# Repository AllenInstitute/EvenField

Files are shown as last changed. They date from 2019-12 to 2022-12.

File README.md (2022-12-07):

# EvenField - An easy, cost effective alternative to commercial based illumination systems for fluorescence microscopy

Coherent laser sources with Gaussian output profiles have been a preferred choice in many optical microscopy systems due to their high spatial intensity and monochromaticity. While these traits can beneficial in many applications, the high spatial coherence of these lasers results in interference effects as the light propagates through various optics toward the sample plane. These inference patterns superimposed onto the Gaussian laser profile result in an uneven illumination of the sample that get transferred into resulting images. For applications such as single molecule fluorescence imaging, the resulting field inhomogeneity  often clouds the signal that is to be detected. In addition, when these sources are used for imaging large areas that require tiling of multiple fields of view, the circular 2D illumination profile excites a larger field of view than is captured by the camera resulting in additional, unneeded photobleaching of these areas.

A simple deployment of a square multimode fiber between the illumination source and destination corrects this issue; however, the propogation of multiple laser modes through the fiber increases the potential for interference and results in additional laser speckle noise in the output beam. Researchers have developed several solutions to circumvent the laser speckle problem including, fiber vibration, tunable oscillating lenses, and spinning diffusers. 

We test some of these solutions and compare them to a commercial product, the Borealis system by Andor. 

----

Our full evaluation of this system can be found in our preprint : 
https://www.biorxiv.org/content/10.1101/2021.04.20.440683v1
  
---
  
We converged on a simple, cost-effective solution which we call the EvenField Illumination system. 

## So you're interested in building the EvenField system? ...We've got you covered.

This repository contains all of the information you will need to get started on building and employing the Evenfield system in your lab. This system can be used on a traditional, commercial laser launch or can be combined with the open source [Nicolase 3500] diode combiner and fiber launch for a cost effective, total solution for your illumination needs.

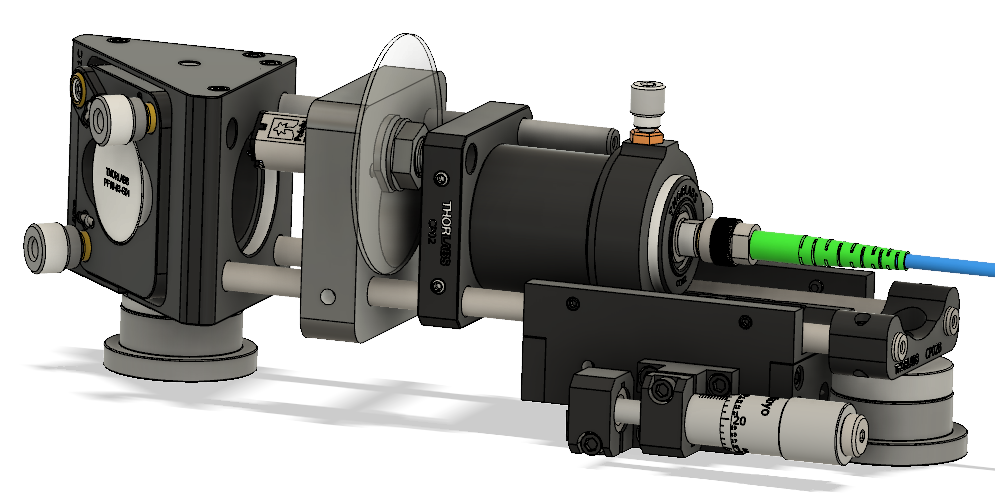
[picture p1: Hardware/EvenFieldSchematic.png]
EvenField System


#### Hardware:
A complete list of associated hardware can be found [here](/Hardware).

This folder contains everything needed to build the EvenField system, including: 

* A complete [bill of materials] (optics and mounts)
* CAD renderings and .STEP files for the spinning diffuser component
* Details on custom optical fiber from Mitsubishi Cable Industries (MCI).
* Illuminator module for easy sensor size matching
* *Coming Soon:* Optical alignment guide 

#### Analysis:
The analysis code used for the EvenField publication has also been provided within this repo and may prove useful for evaluating the field flatness of your system. Code was written in Python and can be found [here].

[Nicolase 3500]: https://github.com/PRNicovich/NicoLase 
[bill of materials]: https://github.com/AllenInstitute/EvenField/blob/master/Hardware/EvenField%20Parts%20List.md
[here]: https://github.com/AllenInstitute/EvenField/tree/master/Analysis

#### Zoom illuminator update
Building on the published EvenField coupler and illuminator design, we implemented a microscope illuminator that features straightforward alignment and sensor-shape matching.  Illumination energy is delivered through an optical fiber - the details of which are not critical for use - and into a homogenizing prism.  The square exit face of this prism is imaged by a commercially-available zoom camera lens and a tube + objective lens pair to the sample plane.  Adjustments to the size and focus of the illumination field are straightfoward using the zoom and focus rings on the camera lens. On its own this assembly provides a simple and cheap square-field illumninator that will work with a wide range of detection camera formats.  Together with the EvenField homogenizer and NicoLase laser launch you can build your own microscopy illumination platform with custom laser power, color, and timing, evenly distributed over a field matching the detection camera FOV.  Add a chassis, cube, objective, and camera, and you've got a fluorescence microscope.

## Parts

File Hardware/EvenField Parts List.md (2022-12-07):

# EvenField V1 Parts List
------------------
### EvenField Speckle Reduction Scheme:
    1 x Edmund Optics #47-989, 0.5° Diffusing Angle 50 mm Dia Mounted (Holographic Diffuser)
    1 x Pololu 3036, 5:1 Micro Metal Gearmotor HPCB 12V (EvenField Version 1 motor, used in manuscript)
    1 x Custom Milled Assembly (see associated CAD)
    
### Optics: 
    1 x Thorlabs PF10-03-G01, Ø1” Protected Aluminum Mirror
    1 x Thorlabs C220TMD-A, f = 11.00 mm, NA = 0.25, Mounted Geltech Aspheric Lens

### Mounting:
    1 x Thorlabs KCB1C, Right-Angle Kinematic Mirror Mount with Smooth Cage Rod Bores
    1 x Thorlabs SM1L10, SM1 Lens Tune 1.00” Thread Depth
    1 x Thorlabs S1TM09, Mounted Aspheric Lens Adapter
    1 x Thorlabs CP02, SM1-Threaded 30 mm Cage Plate
    1 x Thorlabs CT102, XY Translation Mount
    1 x Thorlabs CT1, Cage Translation Stage
    1 x Thorlabs SM05FC, FC/PC Fiber Adapter Plate with External SM05
    1 x Thorlabs CP02B, Snap-On 30 mm Cage Mounting Bracket, 8-32 Tap
    2 x Thorlabs RS05P, Ø1" Pedestal Pillar Post, 1/4"-20 Taps, L = 0.5"
    1 x Thorlabs RS3M, Ø25 mm Post Spacer, Thickness = 3 mm
    1 x Thorlabs RS6M, Ø25 mm Post Spacer, Thickness = 6 mm
    1 x Thorlabs ER3, Cage Assembly Rod, 3” Long
    2 x Thorlabs ER6, Cage Assembly Rod, 6” Long

### Fiber:
    1 x Custom Multimode Square Core Fiber from Mitsubishi Cable Industries, LTD., 600 µm x 600 µm core, 0.15 NA P/N: KV95P2 ST600SQH 
     OR
    1 x Thorlabs M43L05, Ø105 µm, 0.22 NA, Low OH, FC/PC-FC/PC Fiber Patch Cable, 5 m

### Output Collimator:
	  1 x Edmund Optics 88-379, 10X Objective, Nikon CFI Plan Fluor
	   OR
	  1 x Thorlabs PAF2P-18A, FiberPort, FC/PC, f=18.4 mm, 350 - 700 nm, Ø3.01 mm Waist
		       Note: Mitsubishi MM fiber has a very large fiber core (600 µm x 600 µm). Due to its size, using the 10X Objective          
                       is the preferred collimation option to avoid vignetting; however, this option introduces additional optical 
                       alignment complexities. 

### Zoom illuminator:

The following parts form a critical illumiator to couple an output fiber into a square prism, then project the prism exit face to the sample plane.  The following components were used in combination with a Nikon Ti2 and Iris15 camera.  The zoom lens adjustments allow for straightforward matching of the illumination and collection areas with minimal light outside of this region.  Using the square prism avoids the need for a square-core fiber and additional magnification in this application.  

	1 x Thorlabs SM2A54 
	2 x Thorlabs LCP01T
	1 x Thorlabs LCP33
	1 x Thorlabs CXY1A
	1 x Thorlabs SM2N1
	1 x Thorlabs TTL200-A (or appropriate tube lens for your system)
	1 x Thorlabs KCB2C
	1 x Thorlabs BB2-E02
	4 x Thorlabs ER05
	1 x Thorlabs RS3P8 + 1 x RS6P8 (exact lengths will vary depending on mounting height)
	1 x Thorlabs RSH3

	1 x Edmund 54-363 Computar 10x close-focus C Mount zoom lens
	1 x Edmund 48-582 2 mm x 2 mm light pipe, or similar (Lumencor screw-on light pipe used in demo)

	1 x hastyCelestaAdapter.stl or equivalent for specific light pipe used

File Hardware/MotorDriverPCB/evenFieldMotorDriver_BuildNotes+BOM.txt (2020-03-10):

Evenfield motor driver

Motor driver allows PWM speed control and power with cheap wall wart supply.  Changing resistance on variable resistor R2 changes duty cycle of pulse train from 555 from ~1% to ~99%.  Native pulse train should stay at at ~14 kHz. This pulse train drives Adafruit TB6612 breakout, which drives the motor.  

Board layout is for 0.1" protoboard. Since this is for protoboard, all through-hole parts are required.  Beyond that the form factor of parts is less important.  Is a simple circuit, too, so there's plenty of tolerance for substitutions.  A printed PCB would be straightforward to design in the future.  

Power was supplied with a 12V wall wart, input through a through-hole jack at JP2 and JP3 positions. I swapped those positions for a power jack with proper pin-out (center is VCC, far side is GND) that fit on a 0.1" protoboard.  

Operation is to screw motor leads into terminal block, plug in power supply, then turn on with toggle switch.  Adjust R2 resistance until a nice balance is found between motor speed and noise/vibration.  Lower speed should optimize for motor life.  Then you can power on/off with switch or by AC supply for future operation. 

BOM:
TB6612 breakout - https://learn.adafruit.com/adafruit-tb6612-h-bridge-dc-stepper-motor-driver-breakout
555 DIP IC - Mouser 595-NE555P
7805 5V regulator - Mouser 926-LM7805CT/NOPB
DPST switch - Nidek Copal Electronics ATE1E-2M3-10-Z
10 nF capacitor - Mouser 594-D103Z25Z5VF63L6R or similar
100 nF capacitor - Mouser 594-K104K15X7RF53H5 or similar
0.1 μF capacitor - Mouser 647-UVR2A0R1MDD1TA or similar
0.22 μF capacitor - Mouser 647-UVR2AR22MDD1TD or similar
10 kΩ resistor - Mouser 279-CFR25J10K or similar
2 x 1N4148 diode - Mouser 512-1N4148 or similar
100 kΩ variable resistor - Mouser 652-3296W-1-104LF or similar
1 x 10 header strip - Adafruit 392 or similar
1 x 6 header strip - Adafruit 392 or similar
1 x 2 Screw terminal block - Adafruit 2138 or similar

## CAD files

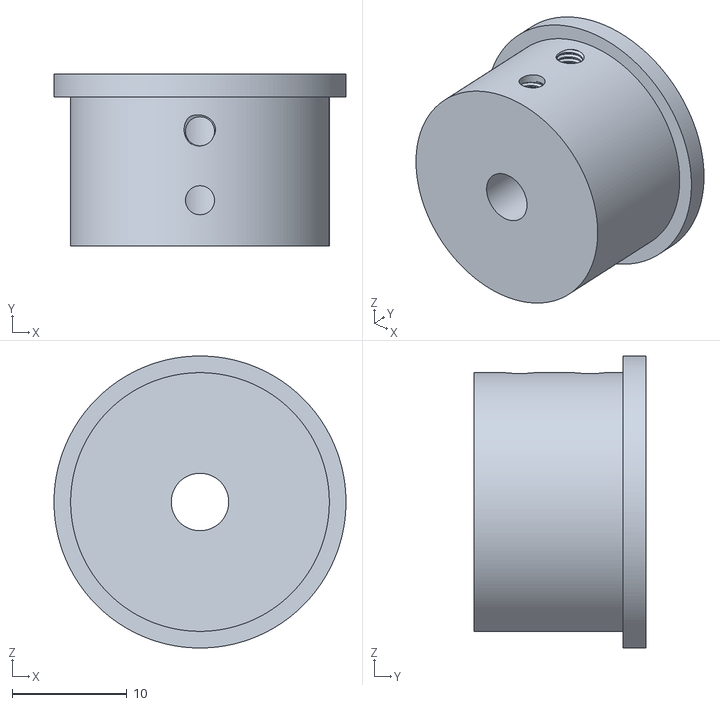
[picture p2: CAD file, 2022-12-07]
Hardware/CAD/hastyCelestaAdapter.stl
25.4 x 15.0 x 25.4

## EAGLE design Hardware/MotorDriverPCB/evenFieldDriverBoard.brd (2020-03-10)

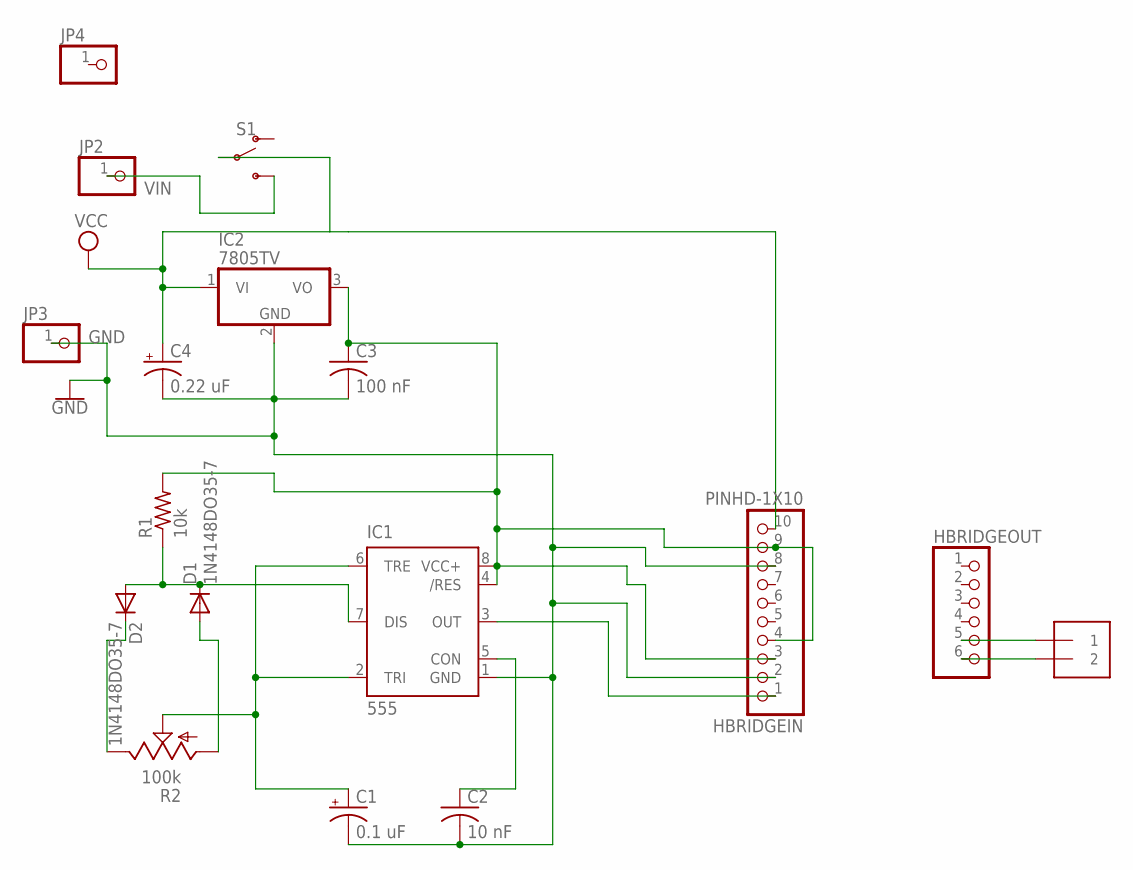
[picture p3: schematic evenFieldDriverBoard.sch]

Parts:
C1: 0.1 uF; B45181A
C2: 10 nF; C025-025X050
C3: 100 nF; C025-025X050
C4: 0.22 uF; B45181A
D1, D2: 1N4148DO35-7; DO35-7
HBRIDGEIN: PINHD-1X10; 1X10-BIG
HBRIDGEOUT: PINHD-1X6; 1X06
IC1: 555; DIP08
IC2: 7805TV; TO220V
J1: 1X2-3.5MM
JP2, JP3, JP4: PINHD-1X1; 1X01
R1: 10k; 0309V
R2: 100k; RJ9W
S1: SWITCH-SPDT-PTH-11.6X4.0MM; SWITCH_SPDT_PTH_11.6X4.0MM

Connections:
GND: C1.-, C2.2, C3.2, C4.-, HBRIDGEIN.2, HBRIDGEIN.8, IC1.1 (GND), IC2.2 (GND), JP3.1
unnamed: C3.1, HBRIDGEIN.3, HBRIDGEIN.4, HBRIDGEIN.9, IC1.4 (/RES), IC1.8 (VCC+), IC2.3 (VO), R1.2
unnamed: D2.C, R2.E
unnamed: D1.A, R2.A
unnamed: C1.+, IC1.2 (TRI), IC1.6 (TRE), R2.S
unnamed: C2.1, IC1.5 (CON)
unnamed: D1.C, D2.A, IC1.7 (DIS), R1.1
unnamed: HBRIDGEIN.1, IC1.3 (OUT)
unnamed: HBRIDGEOUT.5, J1.1
unnamed: HBRIDGEOUT.6, J1.2
VCC: C4.+, HBRIDGEIN.10, IC2.1 (VI), S1.2
VIN: JP2.1, S1.3 (S)

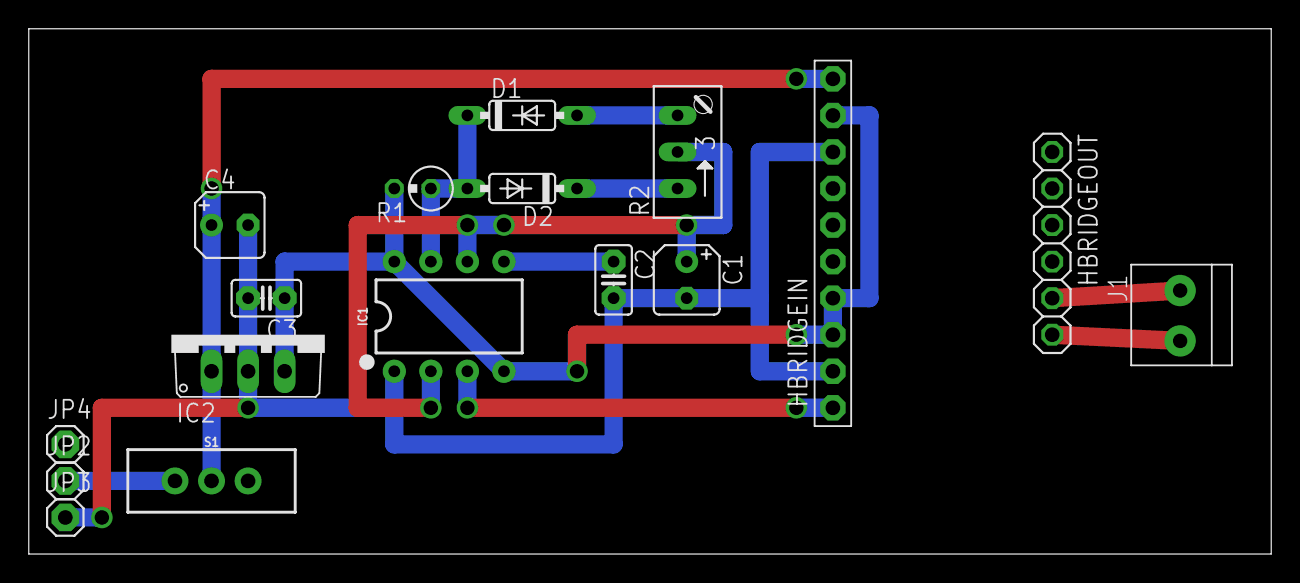
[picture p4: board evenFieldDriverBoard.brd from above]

Board: 2 copper layers, 86.3 x 36.5 mm, 17 parts (0 on the bottom side), 12 nets.

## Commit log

2019-12-17 Fixed CAD import issues to SolidWorks
    [0213-904-00 v1_1.sldasm, 0213-904-01_1.sldprt, 0213-904-02.sldprt, 0213-904-03_1.sldprt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]
2020-01-02 Change CAD to .STEP
    [0213-904-00 v1_1.sldasm, 0213-904-01_1.sldprt, 0213-904-02.sldprt, 0213-904-03_1.sldprt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]
2020-01-02 1) Add analysis output .JSON files for manuscript data 2) Add CAD of EvenField system with NicoLase 3500 diode laser combiner
2020-03-09 Adding in motor driver PCB files.
    [evenFieldDriverBoard.brd, evenFieldDriverBoard.sch]
2020-03-09 Added build notes and BOM for motor driver board.
    [evenFieldDriverBoard.brd, evenFieldDriverBoard.sch]
2020-03-09 Update PCB build notes.
2022-06-17 Adding in info for the zoom illuminator.
    [hastyCelestaAdapter.stl]

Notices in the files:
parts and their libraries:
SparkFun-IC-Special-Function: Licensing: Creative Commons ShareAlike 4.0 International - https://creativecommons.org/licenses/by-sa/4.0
